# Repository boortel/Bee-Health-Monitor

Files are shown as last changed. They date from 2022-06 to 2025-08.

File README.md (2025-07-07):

# Bee Health Monitor project

The aim of this project is to design an open-source project, which would be done from commonly available modules using 3D printing technology.

## Which device is presented there?

This is a second version of the bee health monitor device, which was developed after evaluating the initial measurements with the original device. This version is designed to be realised by anyone at home with commonly available tools, hardware, and a 3D printer. The recommended print material is PETG or ASA as it provides good sunlight and weather durability and can be easily sterilised when moved to the other bee hive. The entire construction is made out of 6 printable parts and a single 2mm plexiglass. An acrylic varnish is applied to improve the water resistance. Using this device, dataset [Bee Dataset BUT-2](https://www.kaggle.com/datasets/imonbilk/bee-dataset-but-2) was collected. This device mounted on the beehive is shown in figure bellow:

Second version of *Bee health monitor* device

The chassis is mentioned to be mounted directly on the entrance to the hive in the way, so the bees are forced to use the 8mm long tunnels on the bottom of the device. The camera field of view is illuminated by a diffused warm white LED. The camera periodically senses bees when passing through the tunnels, as shown in figure bellow:

Sample from the image part of the dataset BUT-2.

The internal electronics consist of commonly available hobby electronic parts and RaspberryPi 4 as a control unit. The sensor equipment consists out of a camera, microphone, two humidity and temperature sensors intend to be placed inside the beehive, CO2 sensor, light sensor and an temperature, humidity and atmospheric pressure sensor to be positioned outside. All data are stored on an internal USB drive in a set interval, and the number of incoming and outgoing bees is evaluated from the camera capture. The main specifications of this device are shown in table bellow:

Device parameters.

## Related research papers

Besides the *Bee Health Monitor* platform, we would like to present our bee related research:

- Bee datasets
  - [Bee Dataset BUT-1](https://www.kaggle.com/datasets/imonbilk/bee-dataset-but-1): dataset collected with the first generation of our device. It contains only image data.
  - [Bee Dataset BUT-2](https://www.kaggle.com/datasets/imonbilk/bee-dataset-but-2): dataset collected with the second generation of our device. It contains image, sound and sensor data.
  - [Bee Dataset BUT-HS](https://www.kaggle.com/datasets/imonbilk/bee-dataset-but-hs): hyperspectral dataset containing images of bees, Varroa mites and detritus.
  - [Bee Dataset BUT-HS2](https://www.kaggle.com/datasets/masuel/bee-hyperspectral-dataset): dataset containing images of bees and Varroa mites under narrow spectra illumination used for the experiments with visual Varroa detection.
 
- Research papers
  -  [Visual Diagnosis of the Varroa Destructor Parasitic Mite in Honeybees Using Object Detector Techniques](https://www.mdpi.com/1424-8220/21/8/2764): article describing the Varroa mite detection using the YOLOv5 network.
  -  [Raspberry Pi Bee Health Monitoring Device](https://arxiv.org/abs/2304.14444): paper describing the communication and remote logging of the *Bee health monitor device*.
  -  [Machine learning and computer vision techniques in continuous beehive monitoring applications: A survey](https://www.sciencedirect.com/science/article/pii/S0168169923009481?dgcid=author): survey article focusing on the visual based bee health monitoring methods. A full version of the paper has a restricted access, a free preprint is available [here](https://arxiv.org/abs/2208.00085).
  -  [Computer Vision Approaches for Automated Bee Counting Application](https://www.sciencedirect.com/science/article/pii/S2405896324004580): paper comparing three possible approaches in the bee counting.
  -  [Varroa destructor detection on honey bees using hyperspectral imagery](https://www.sciencedirect.com/science/article/pii/S0168169924006100?dgcid=rss_sd_all): article describing a possible use of the hypespectral imaging in Varroa mite detection.
  -  [Towards Varroa destructor mite detection using a narrow spectra illumination](https://arxiv.org/abs/2504.06099): paper describing initial experiments with the narrow spectra illumination for Varroa mite detection.
 
- Final thesis
  - [Approximation of functions determining colony activity using neural networks](https://www.vut.cz/studenti/zav-prace/detail/151629): Master thesis describing the development of the setup presented in paper *Raspberry Pi Bee Health Monitoring Device* in a more detail together with further clustering experiments.
  - [Visual Detection of the Parasitic Mites on the Honeybee](https://www.vut.cz/en/students/final-thesis/detail/167591): Master thesis describing the development of the narrow spectra illumination unit and following experiments evolving the findings described in article *Varroa destructor detection on honey bees using hyperspectral imagery*. Summary of the thesis is presented in paper *Towards Varroa destructor mite detection using a narrow spectra illumination*.

## Software

The complete overview of the used software is provided in [software](https://github.com/boortel/Bee-Health-Monitor/tree/main/software) section.

## Hardware

The complete overview of device 3D printing, laser cutting, assembly and inner electrical installation is provided in [hardware](https://github.com/boortel/Bee-Health-Monitor/tree/main/hardware) section.

### Keywords

Bees, Health, Camera, Sensory, Neural Networks, AI

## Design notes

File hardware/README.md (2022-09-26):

# BeeLogger - Hardware setup

The folder contains a brief overview of how the device is constructed.
It contains the .STL and files of 3D printed parts, .DXF file of a laser-cut plastic window and a brief overview of how to assemble the entire device.
Also, the BOM of electronic componentes is apended.

## 3D Printed Parts and Laser Cut

Recommended 3D print infill ~15%

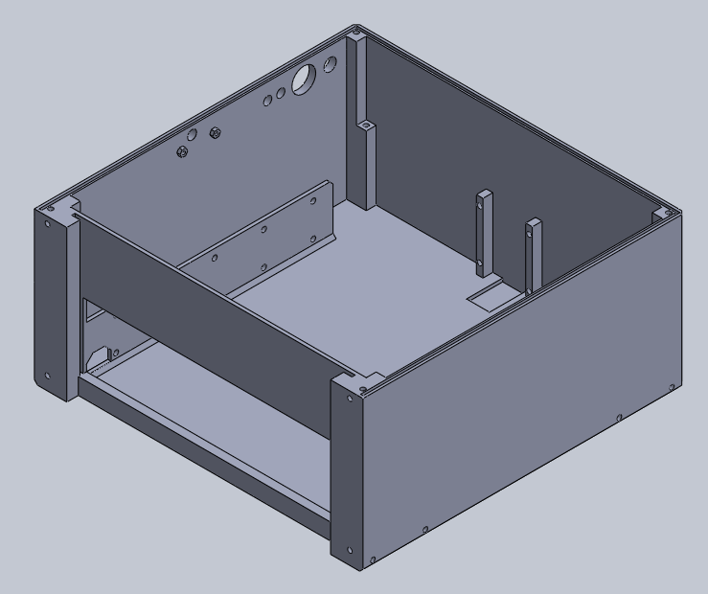
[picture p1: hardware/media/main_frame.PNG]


1x Main frame 

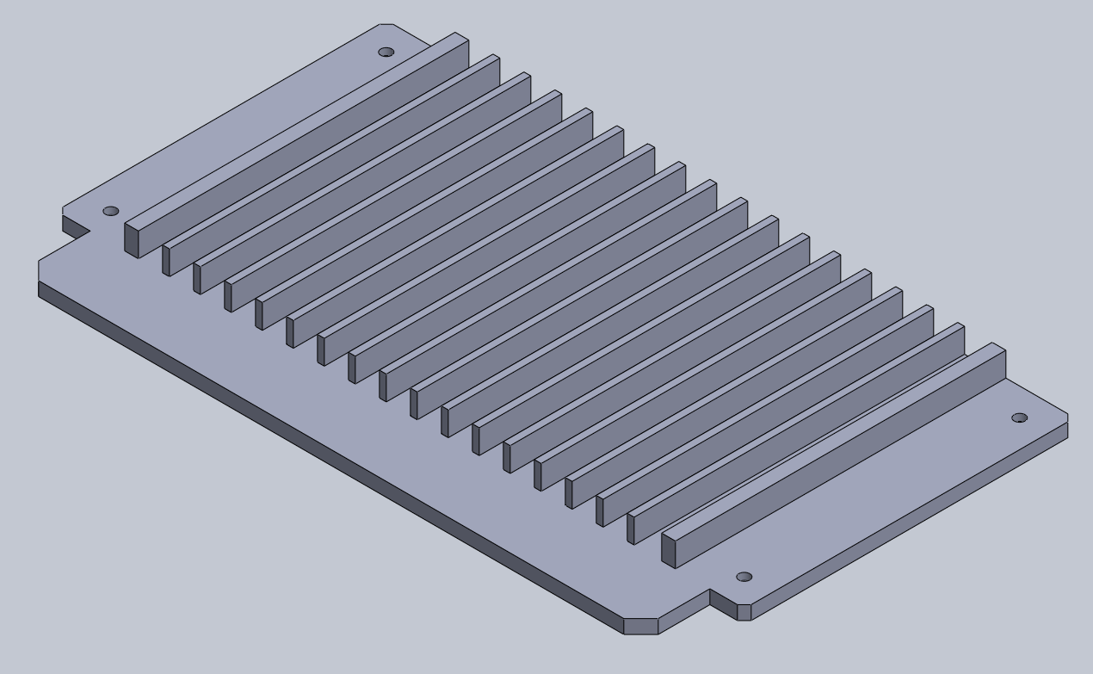
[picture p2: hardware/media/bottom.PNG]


1x Bottom (bee tunnels)

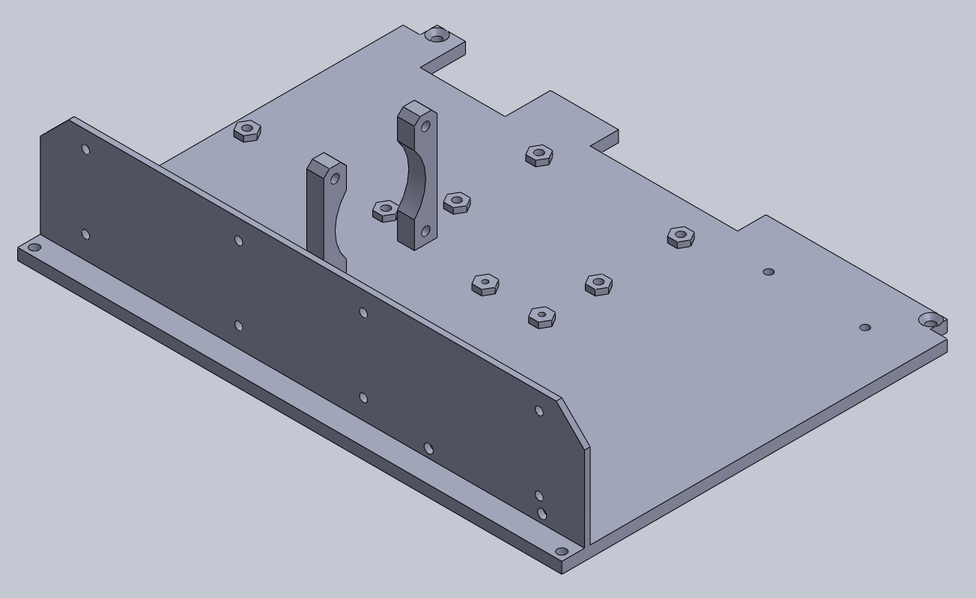
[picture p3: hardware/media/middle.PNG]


1x Middle (electronics mount layer)

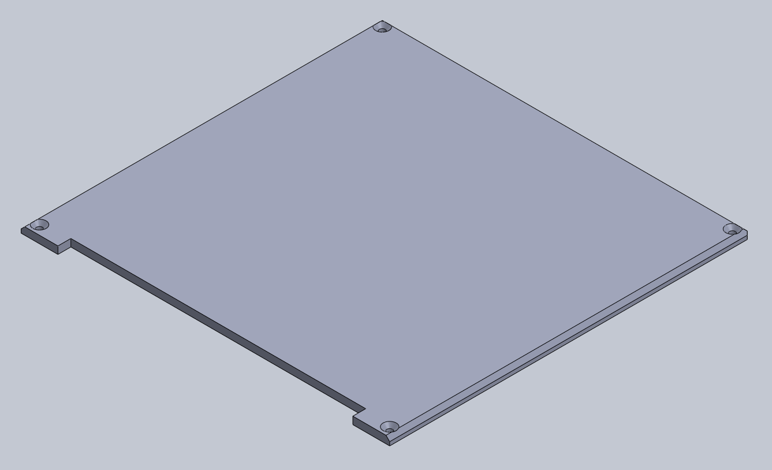
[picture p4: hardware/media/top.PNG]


1x Top cover

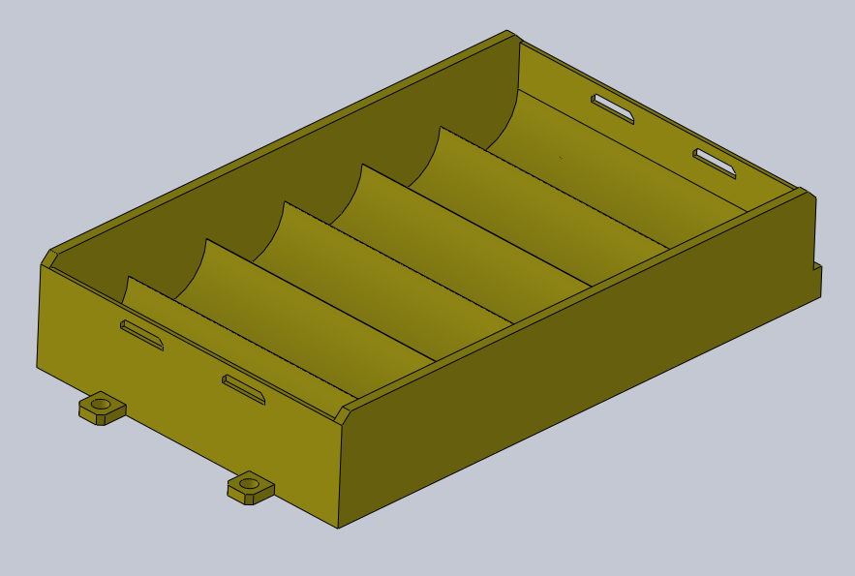
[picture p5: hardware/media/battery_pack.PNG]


1x Battery pack (6x 18650)

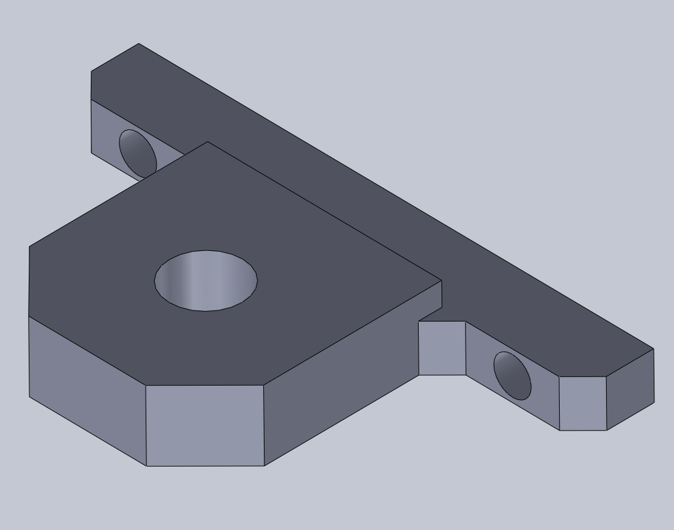
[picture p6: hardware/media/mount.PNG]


4x Helper mount hole

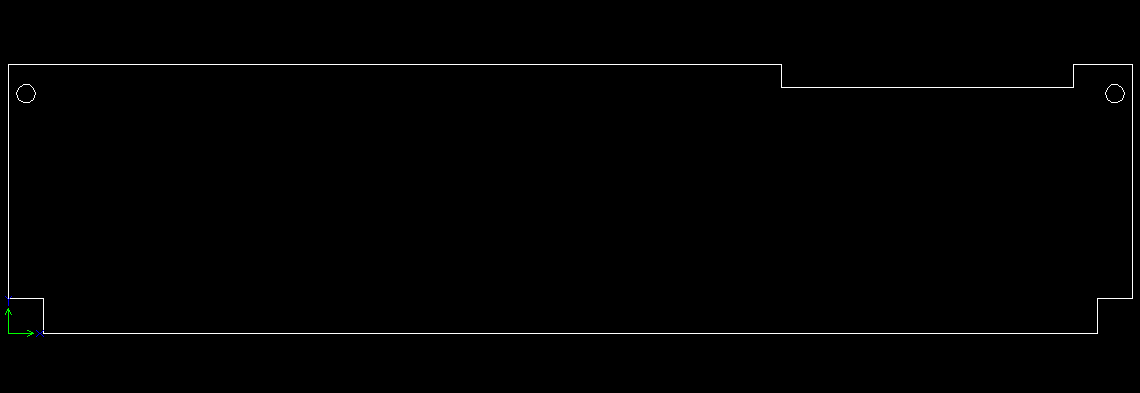
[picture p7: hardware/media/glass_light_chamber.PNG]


1x Laser-cut plastic window. Window suppose to be light diffuser and to be non-transparent. After cutting it, scratch it and glue white paper on it.

## Assembly

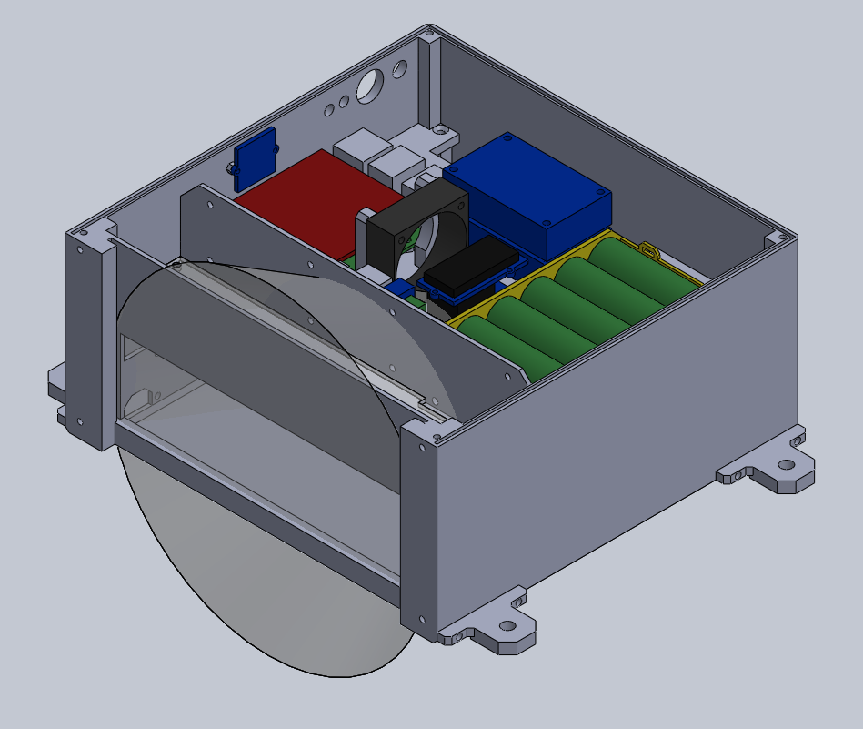
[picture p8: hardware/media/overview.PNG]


Inner layout of the assembled device

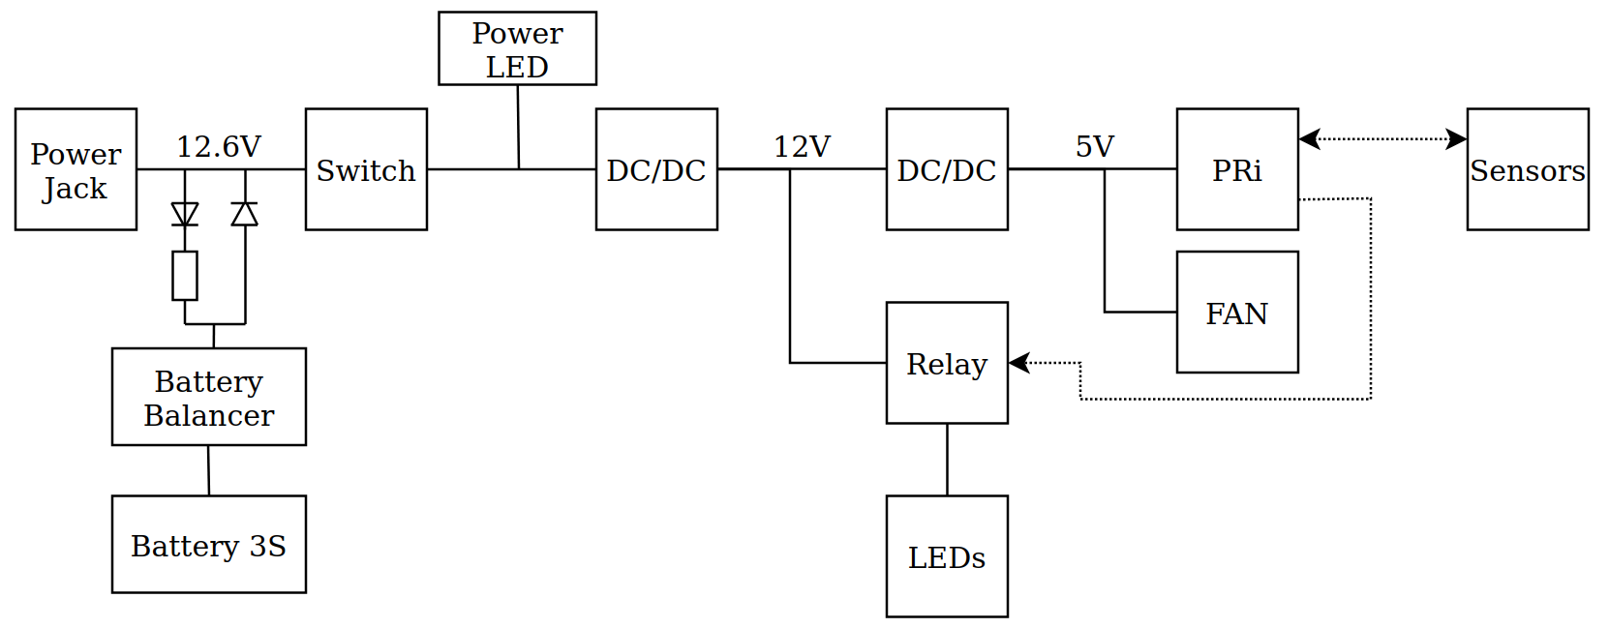
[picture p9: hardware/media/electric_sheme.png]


Electrical scheme. The battery resistor choose in the way, so the charging current will be between 1/10 and 1/100 of a battery capacity. 

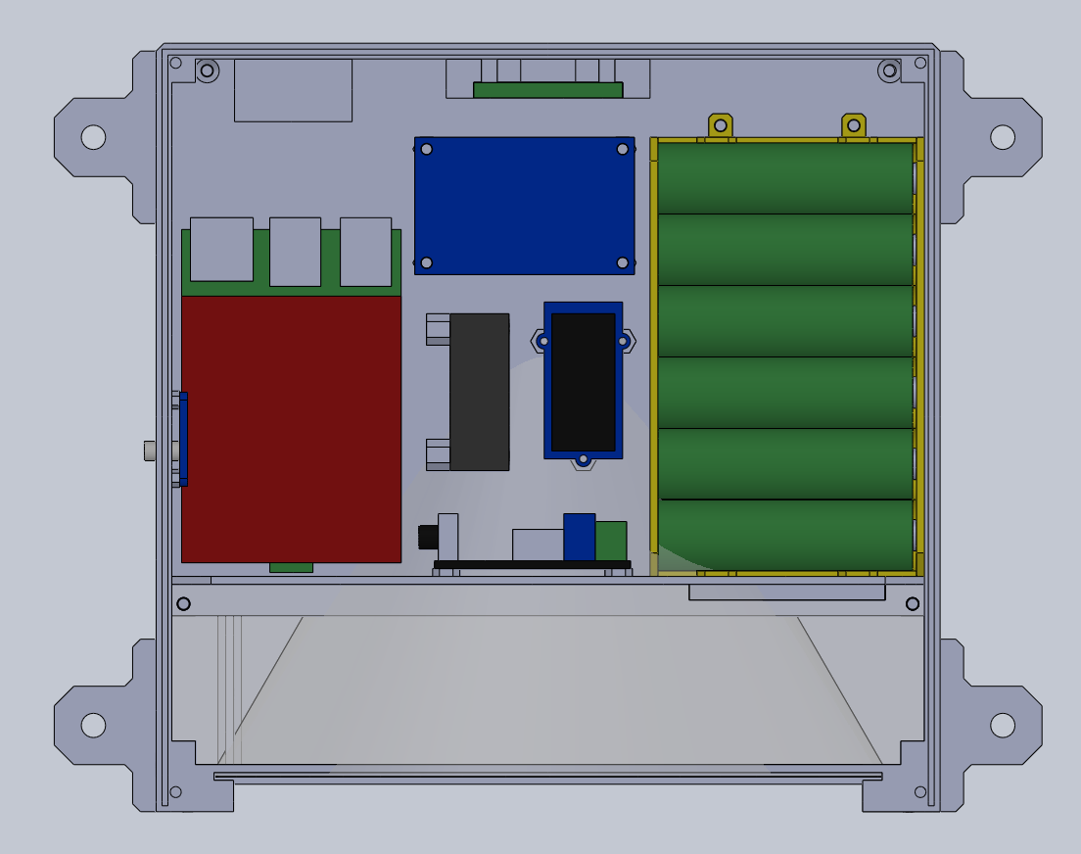
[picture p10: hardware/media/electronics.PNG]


Inner electronics layout

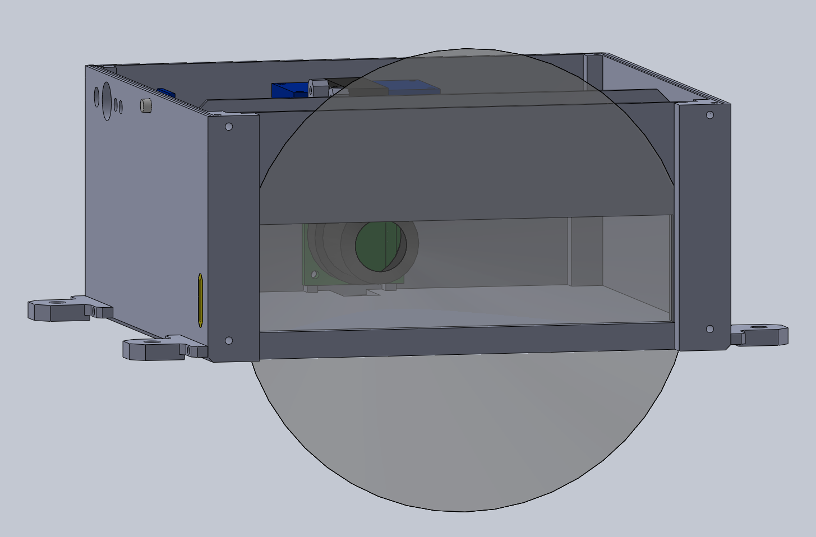
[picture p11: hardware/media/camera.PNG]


Camera's Filed of view

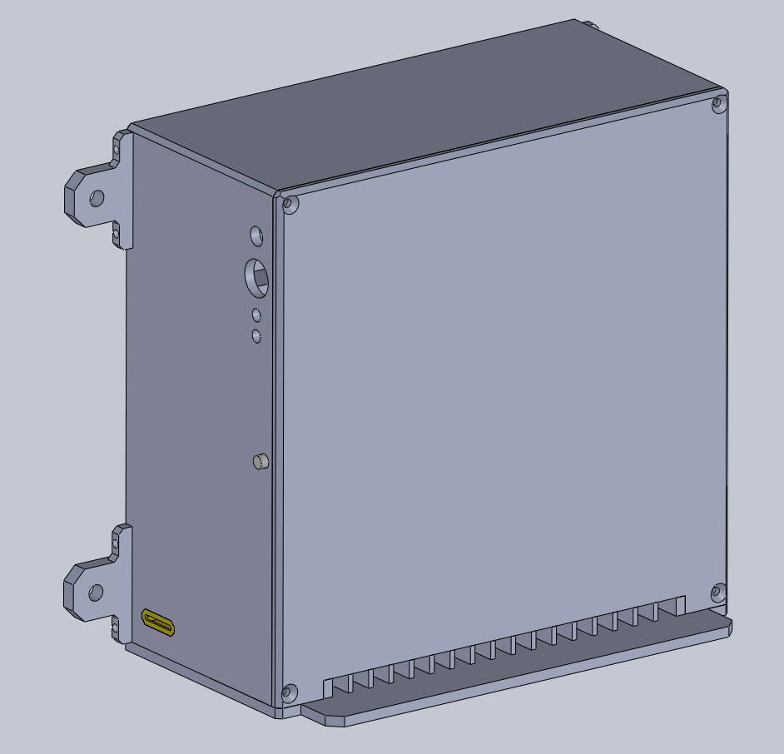
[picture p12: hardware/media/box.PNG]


General overview of the assembled device

## BOM

| Part                                                                                                                                                                                                                                                                                                                                                                                                                                                                                          | Quant. |
|-----------------------------------------------------------------------------------------------------------------------------------------------------------------------------------------------------------------------------------------------------------------------------------------------------------------------------------------------------------------------------------------------------------------------------------------------------------------------------------------------|--------|
| [Raspberry Pi 4](https://www.amazon.com/Raspberry-Model-2019-Quad-Bluetooth/dp/B07TC2BK1X/ref=sr_1_3?crid=3DNPLNTMRC0AU&keywords=raspberry+pi+4&qid=1657797906&sprefix=raspberry+pi+4%2Caps%2C250&sr=8-3)                                                                                                                                                                                                                                                                                     | 1      |
| [RPI HQ Cam](https://www.amazon.com/Arducam-Raspberry-Camera-Sensitivity-Adapter/dp/B09YHN5DBY/ref=sr_1_13?crid=3JH802ACAZP61&keywords=rpi+HQ+camera+lens&qid=1657798011&sprefix=rpi+hq+camera+len%2Caps%2C123&sr=8-13) + lens                                                                                                                                                                                                                                                                | 1      |
| [RPi Grove Shield](https://www.ebay.com/itm/334355129343?hash=item4dd91e63ff:g:mqgAAOSwQSJiJeLv)                                                                                                                                                                                                                                                                                                                                                                                              | 1      |
| [18650 Battery](https://www.amazon.com/dp/B0B6FSJ64C/ref=sr_1_6?keywords=18650+battery&qid=1657797820&s=hpc&sr=1-6)                                                                                                                                                                                                                                                                                                                                                                           | 6      |
| [Bat. Balancer](https://dratek.cz/arduino/1675-ochranny-modul-pro-li-ion-lithiovou-baterii-3s-11.1v-12.6v-25a.html?hp=&mena=2)                                                                                                                                                                                                                                                                                                                                                                | 1      |
| [DC/DC conv.](https://dratek.cz/arduino/1332-lm2596-buck-step-down-napajeci-modul-dc-4.0-40-1-3-37v-led-voltmetr.html)                                                                                                                                                                                                                                                                                                                                                                        | 2      |
| [Grove RTC](https://www.ebay.com/sch/i.html?_from=R40&_trksid=p2380057.m570.l1313&_nkw=grove+rtc&_sacat=0)                                                                                                                                                                                                                                                                                                                                                                                    | 1      |
| [DHT11](https://www.ebay.com/sch/i.html?_from=R40&_trksid=p2334524.m570.l1313&_nkw=DHT+11&_sacat=0&LH_TitleDesc=0&_odkw=grove+rtc&_osacat=0&LH_PrefLoc=2)                                                                                                                                                                                                                                                                                                                                     | 1      |
| [ENV3](https://rpishop.cz/senzory/4241-m5stack-env-iii-unit-se-senzorem-teploty-tlaku-a-vlhkosti-sht30qmp6988.html)                                                                                                                                                                                                                                                                                                                                                                           | 1      |
| [Grove Light Sensor](https://www.ebay.com/itm/115371780148?hash=item1adcb1a834:g:p5cAAOSw2lJijgGw&amdata=enc%3AAQAHAAAAsMwhKJOG7uEdWDz4aTTYPmgAQlXo4PAaFRxJYsTsN9ZDW8MtpcHMV4V%2Bhsg6oTzNw7bdYWFqKl9zcnKPQoEQt9o9jaSmYsWy3%2FuPxQbv%2F4rcpWA%2B3RqnVxn2d0qufJDMz87yKeJ0pvAH3CqHeBTu3Sl8CeBe4ytG7H0gK%2BD5vQbvUEcoCBuCv5cKKdVN2OFY7ayYmmd9%2BgUY6EnRWcesdm7kwgKTsANZybKgTvEvVADu%7Ctkp%3ABk9SR7TF1ce_YA)                                                                                       | 1      |
| [SGP30](https://www.ebay.com/itm/195140387077?hash=item2d6f460105:g:IV4AAOSwALliqovs&amdata=enc%3AAQAHAAAAoEYILUQBEA1M2qm9553zE1rYK8iZPUOqDFQ5M0U1%2F%2B7h1hD%2BO74fW6GdsqcuCPavIPDtD9BcmCXtbAdXqlqqsORFQD5AdWnqxj%2BqtnaFJ7cUh0A4W07rTO8RLcktgtYs15OxcXUyz%2BfB%2FDxUMdCkDCPD%2F7KCfHI3Wk3ZXtxuI%2BLa%2FMzSF8uARfPjLuD0sv1fOlyiwiupCzLwshgyeSRBeoM%3D%7Ctkp%3ABk9SR-yD3se_YA)                                                                                                                | 1      |
| [PWM module](https://www.gme.cz/pwm-regulator-6-28v-3a-product-38323)                                                                                                                                                                                                                                                                                                                                                                                                                         | 1      |
| White LED Strip (~5W)                                                                                                                                                                                                                                                                                                                                                                                                                                                                         | 1      |
| [Grove Relay](https://www.ebay.com/itm/254146781973?epid=22029928343&hash=item3b2c542315:g:EzMAAOSwSsZceRci&amdata=enc%3AAQAHAAAA4O%2B0Wh8ZB8VRDDb%2FWzsDqWErDy%2FSSafImfJD0wpvu4O8v7kF9CB2CKKtg%2BGMNghNTny%2FRScPLqYhwbOtqi4y3yHcN4Nm6020tmhc2842d%2FJ6y06LLDJvED1AmRqOSzUNlqRDt1n2pIq7CMECoP42DbTCAu3oM7Akx2VpHM4BNWExyj2piriykc%2FudUOkO0%2BGr6S1q3tQHmP1vzJkYcNNAeggqim%2Bv1iSXW%2F3%2FaeRGHtFIKr4Xokah2vNsq0NCE6vV5ECmTIgx4qSGdqW1niWqcfyO4UyeRj%2BD3lZ4KXjOPj%2B%7Ctkp%3ABFBMhq7lx79g) | 1      |
| [Fan 40mm 5V](https://www.ebay.com/itm/193494700157?hash=item2d0d2ed07d:g:~h4AAOSwHXxe5R9a&amdata=enc%3AAQAHAAAA4MZ8QLBYeV7MZkPQ7aCef%2FeS%2BUYi0dzfAXOKBU7Zo4sm7spztomIV5cc2MlaOlDPu42ZvmNDGqQX%2B3mkWMrqmf3cN8Dlz27DkY55V6tVkCSmj6hSFUPBTyDseW5LpGHNnjDxnF37DiYTF8kNNkPfArd9EyDPTwA9pWbKx5dlC7pIH6vvy20zI56Copqv5gKE573sLwvWoSqf3IbCN%2BPLXv6VAXJj%2FiGKq7W7P5nI7lhjMEqyEEVWnVKuz9BdJLZP9Y290r86Uu6Ve5wx2erYl9JlciHpBKVwx%2BlAuhTlekcO%7Ctkp%3ABFBM0tXnx79g)                                | 1      |
| [Mic](https://www.ebay.com/itm/354075600684?epid=114811768&hash=item52708ce72c:g:XxAAAOSwwPphWdPQ&amdata=enc%3AAQAHAAAA0MovSSj2B8fCi1UciKMQTruINFD31l0nOGRFHE60S58GoFakqbGCcVotesylyoWFaqIN5MyUQbZzAnNIb0QimNdfYYf2y5Rr0zYdyH%2Fhfd8kVY8AievarkFtJ1cfjrMB8Z52GJsmWBXqa8CGebM%2BvAJqmdpOzCz9i%2BnuoDnG8mN28lzAJt925zVX%2BlFu2YwtTvOwF9b7tAyrJPX1JeAMaM%2FUv9zJn1R%2B%2BnNvEcAJSrfwgm3JkXlF4zdoKQmj9zJJT2a4a20MygMvFRIiBA%2BrXtI%3D%7Ctkp%3ABFBM7rrW0sJg)                                       | 1      |
| M2.5x6 screws                                                                                                                                                                                                                                                                                                                                                                                                                                                                                 | ~ 10   |
| M3x6 screws                                                                                                                                                                                                                                                                                                                                                                                                                                                                                   | ~ 30   |

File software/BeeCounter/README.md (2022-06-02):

# Bee tracker (FicekD)

Please see the original repository: https://github.com/FicekD/Bee-Tracking

This software implements counting of the bees arriving and leaving a hive through the measuring device. Version used in this repository is not a stand-alone application and it does not contain any visualisation tools.

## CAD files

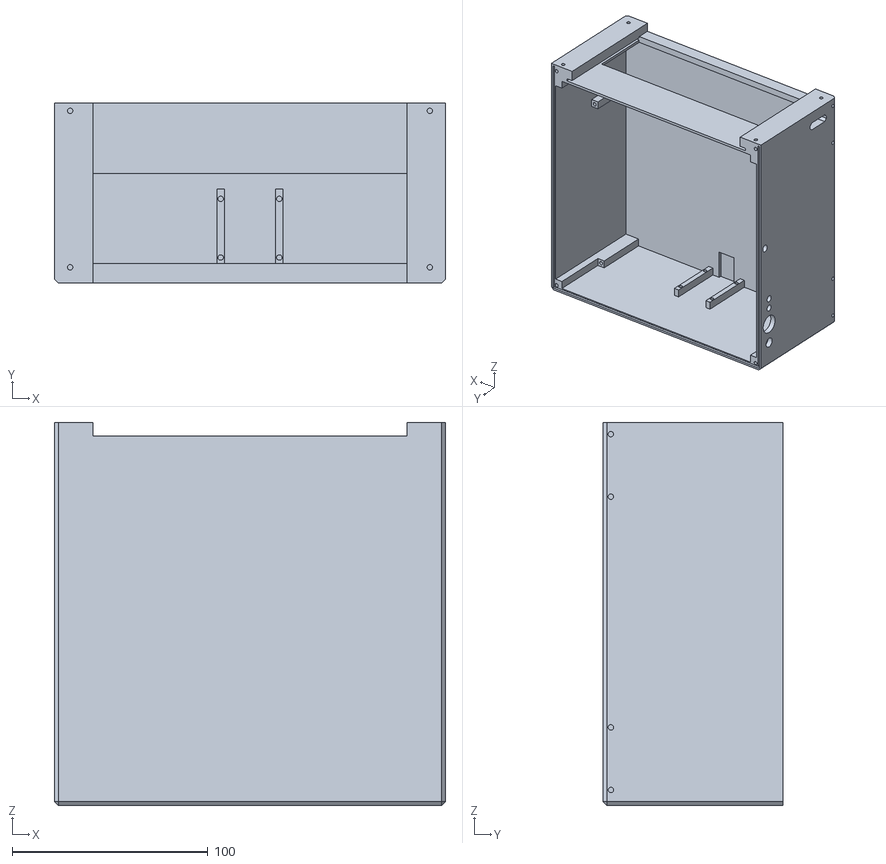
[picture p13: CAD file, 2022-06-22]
hardware/stls/main_frame.STL
200.0 x 92.0 x 196.0

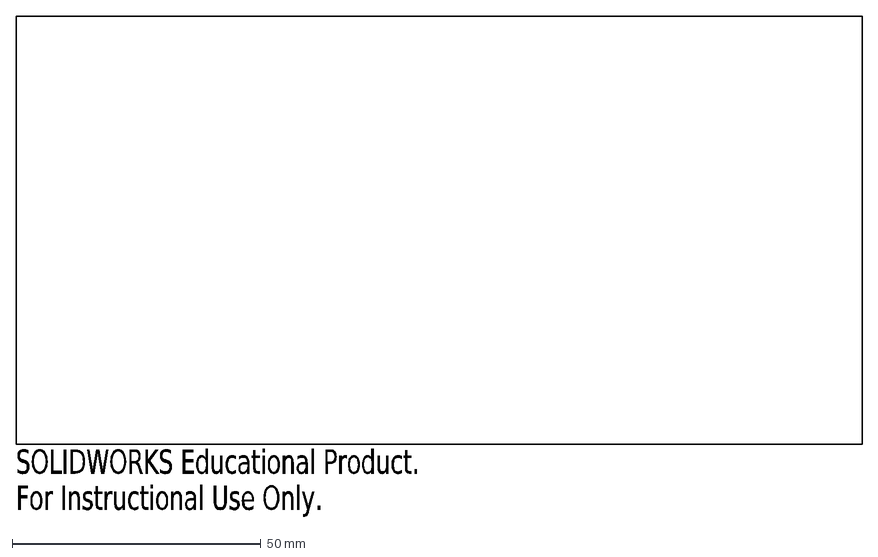
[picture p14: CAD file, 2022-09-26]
hardware/laser_cut/glass.DXF
SOLIDWORKS Educational Product.
For Instructional Use Only.

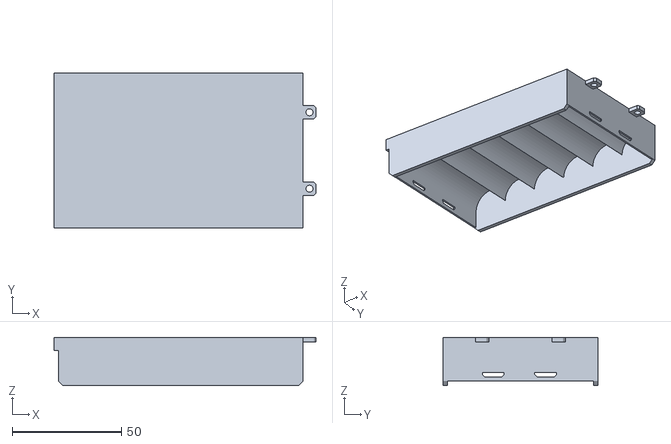
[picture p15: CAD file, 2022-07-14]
hardware/stls/battery_pack.STL
120.0 x 71.0 x 22.0

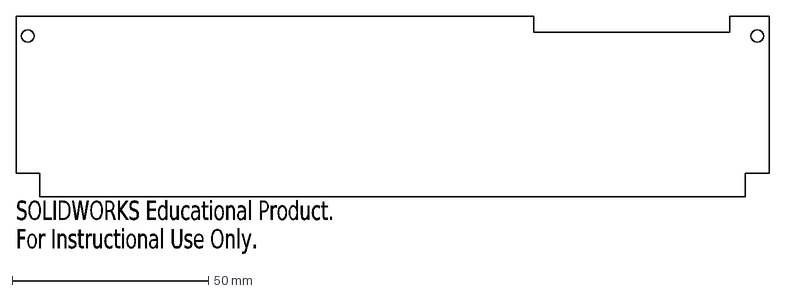
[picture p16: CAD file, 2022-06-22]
hardware/laser_cut/glass_light_chamber.DXF
SOLIDWORKS Educational Product.
For Instructional Use Only.

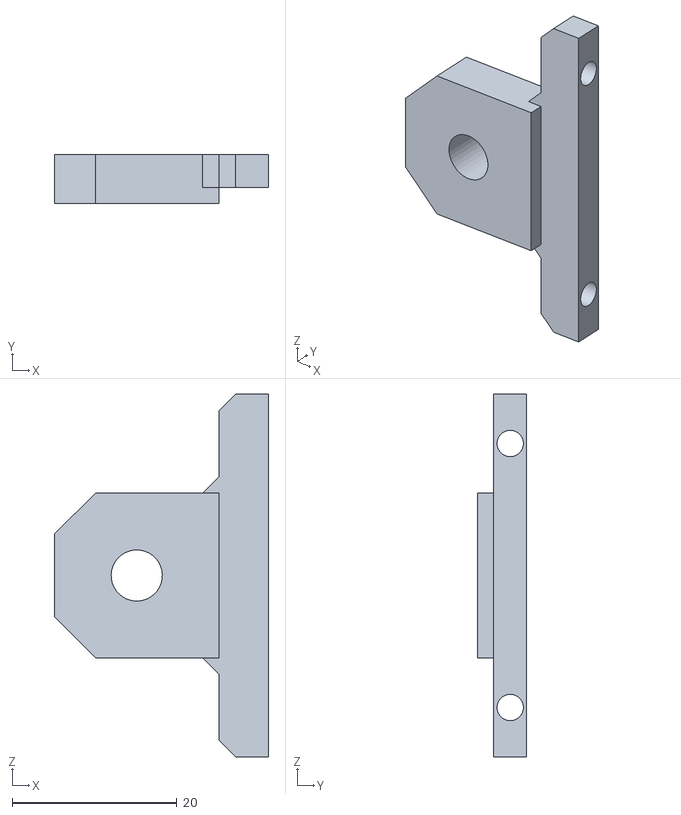
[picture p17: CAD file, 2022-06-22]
hardware/stls/mount.STL
26.0 x 6.00 x 44.0

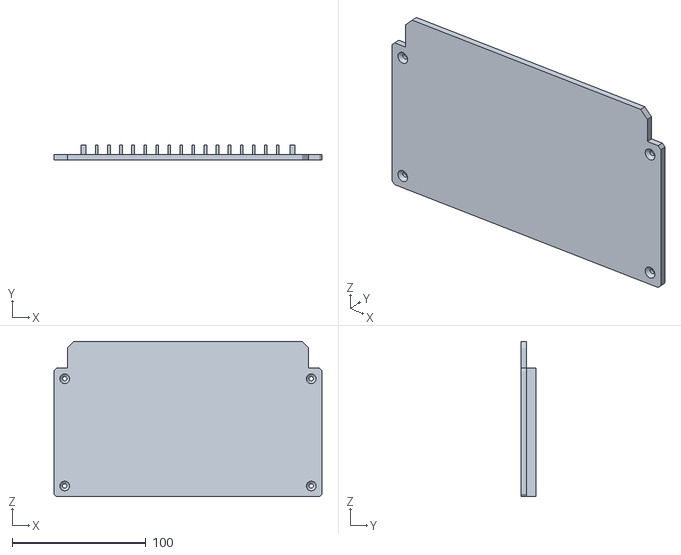
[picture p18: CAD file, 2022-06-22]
hardware/stls/bottom.STL
200.0 x 11.0 x 116.0

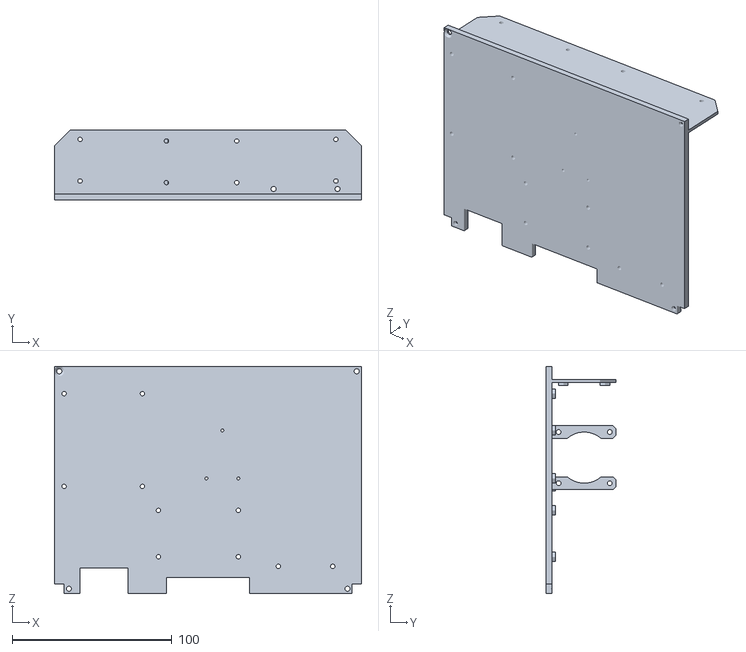
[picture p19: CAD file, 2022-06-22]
hardware/stls/middle.STL
192.0 x 44.0 x 142.0

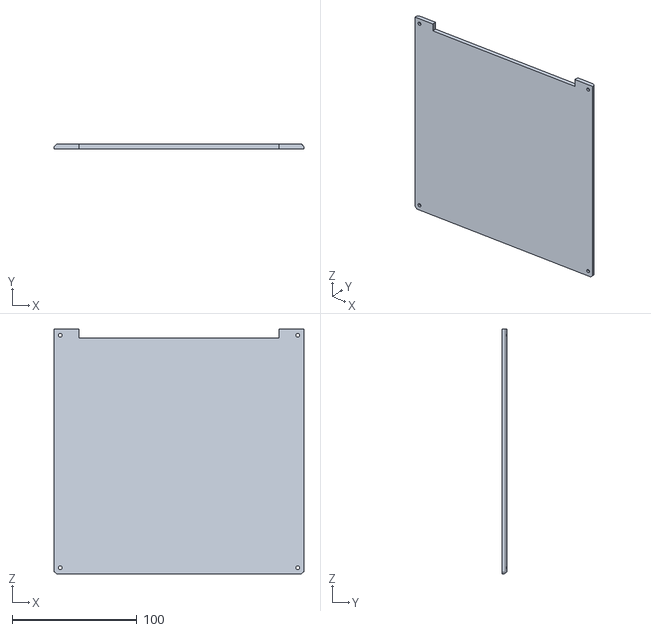
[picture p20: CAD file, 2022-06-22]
hardware/stls/top.STL
200.0 x 4.00 x 196.0

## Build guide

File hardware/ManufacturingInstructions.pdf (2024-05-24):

# Bee health monitor manufacturing instructions

Instructions valid for version 2.1. (summer 2023) | May 2024
| Brno, Czech Republic

## List of contents

## 1. Responsibility disclaimer

Building and using of the proposed device is at your own responsibility. We do not take any responsibility of damage caused by building, or using the Bee Health Monitor device. All information, content, and materials available in this project are for general informational purposes only.

## 2. Introduction

This document describes the assembly of the Bee Health monitor device. Due to the intention of long-term in field measurements, please read this document carefully so you could avoid damaging your device. Basic knowledge in electronics, 3D printing and DYI stuff is needed for the device assembly. Minor deviations from the provided instructions and schemes are possible.
The instructions are valid for the version from summer 2023.

## 3. Preparation phase

This chapter describes the required steps prior the mechanical and electrical assembly.

### 3.1. Electronic modules preparations

Prepare the PWM module, DC-DC convertor, rPi camera, rPi4 and the sensor modules as shown in Figure 1. Fill all connectors with electric insulating vaseline (preferably TPFE) and paint the circuit boards with a suitable varnish designed for the use on electronics. This is required to avoid potential damage caused by humidity. Be careful not to paint over camera chip or any contacts.

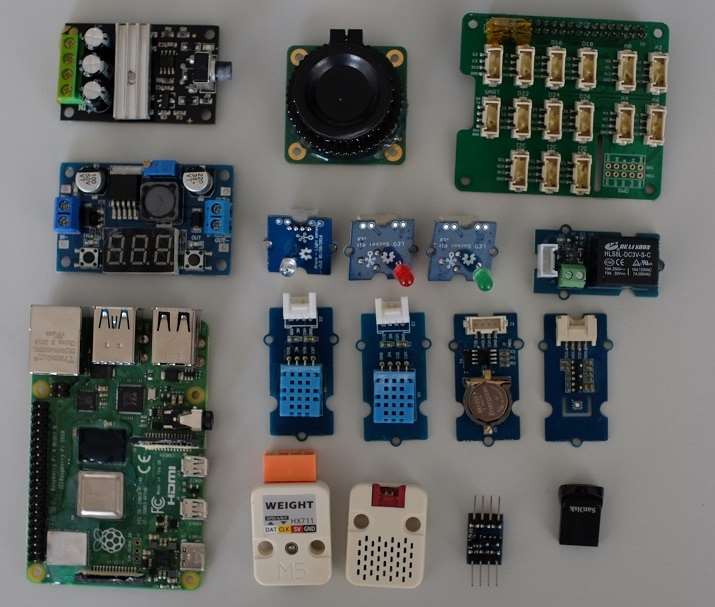
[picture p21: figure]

Figure 1 Required HW and electronic modules As few of the rPi chips and components are BGAs, please seal their surroundings using silicone intended for electronics. Mounting passive cooling is also recommended.

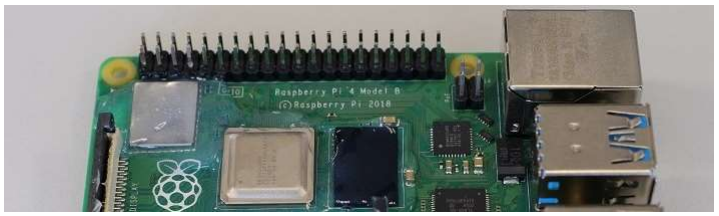
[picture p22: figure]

Figure 2 MCU sealings

### 3.2. Mechanical part preparations

Print all the 3D parts from the Bee-Health-Monitor/hardware/stls/ directory. Prepare the LED strip on aluminum plate and cut the M3 threads to the plate. Prepare the laser cut plexiglas from the directory Bee-Health-Monitor/hardware/laser_cut/ and brush the diffusing plate as shown in Figure 3.

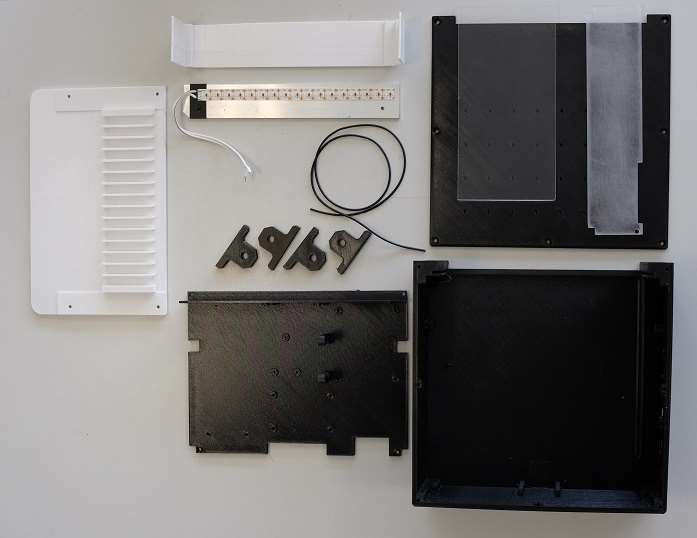
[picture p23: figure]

Figure 3 Printed 3D parts, laser cuts, LED plate and sealing gasket The main box and cover should be sprayed with a primer varnish with filler to seal small gaps caused by the 3D printing. The back side of cover plate and the inner side of the box opposite the diffuser plate should be painted with a matt white to improve the illumination conditions (diffuse the light) as shown in Figure 4.
After spraying the exterior of the main box and cover with a primer, use an acrylic varnish of a proper color to improve the protection and place the sealing gasket to the rabbet in the main box.

## 4. Mechanical assembly

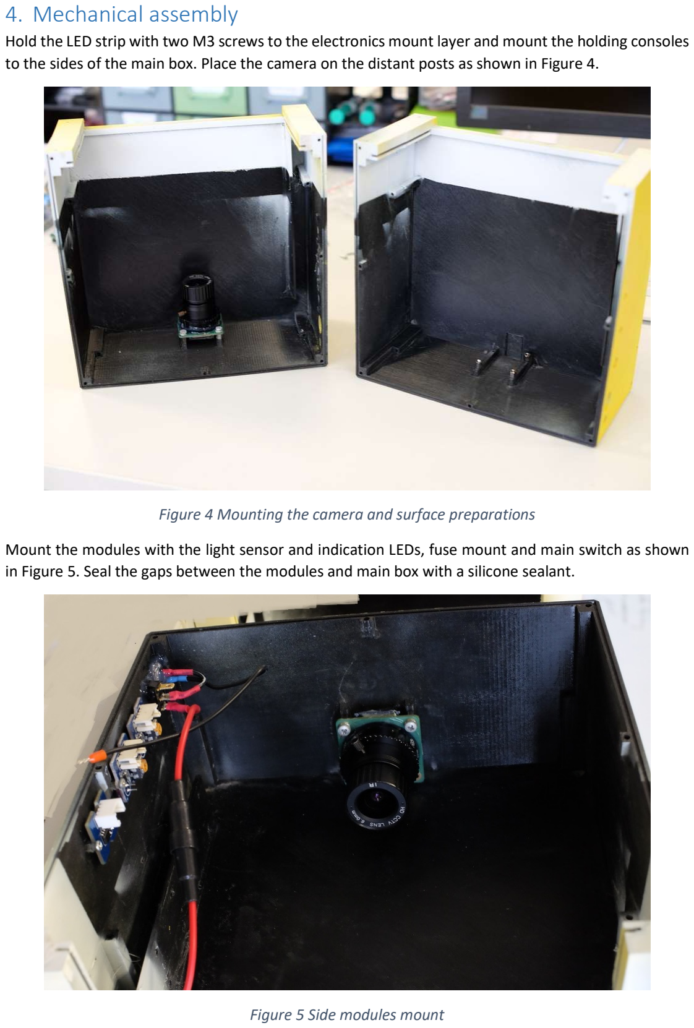
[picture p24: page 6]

Hold the LED strip with two M3 screws to the electronics mount layer and mount the holding consoles to the sides of the main box. Place the camera on the distant posts as shown in Figure 4.

Figure 4 Mounting the camera and surface preparations Mount the modules with the light sensor and indication LEDs, fuse mount and main switch as shown in Figure 5. Seal the gaps between the modules and main box with a silicone sealant.

Figure 5 Side modules mount

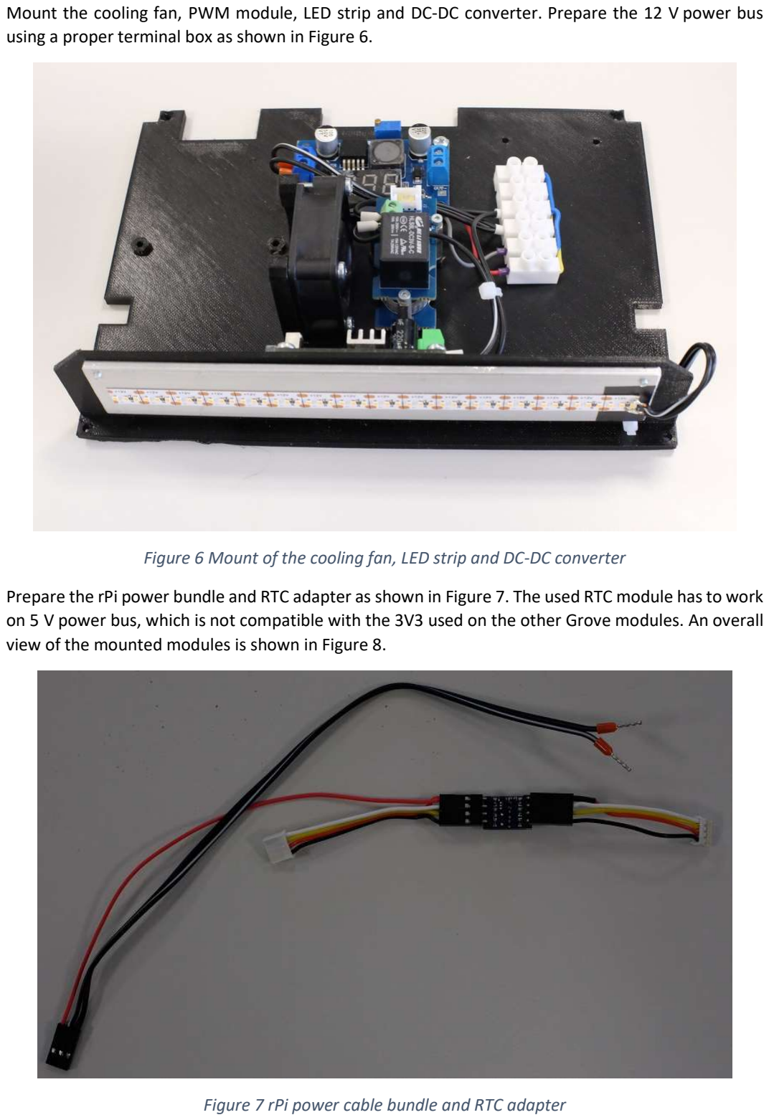
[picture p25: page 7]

Mount the cooling fan, PWM module, LED strip and DC-DC converter. Prepare the 12 V power bus using a proper terminal box as shown in Figure 6.

Figure 6 Mount of the cooling fan, LED strip and DC-DC converter Prepare the rPi power bundle and RTC adapter as shown in Figure 7. The used RTC module has to work on 5 V power bus, which is not compatible with the 3V3 used on the other Grove modules. An overall view of the mounted modules is shown in Figure 8.

Figure 7 rPi power cable bundle and RTC adapter

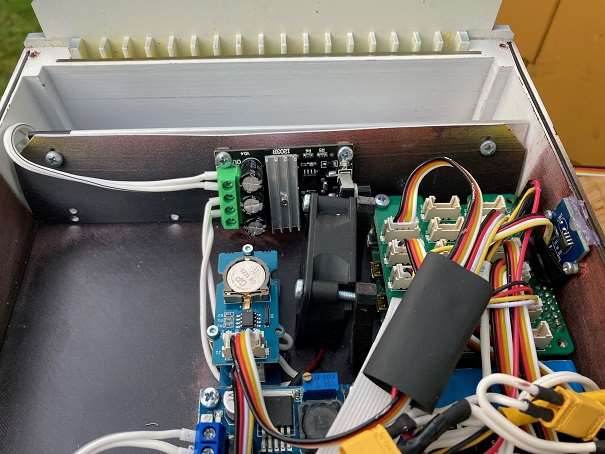
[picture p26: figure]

Figure 8 Overall assembly of interval electronics

## 5. Electrical assembly

Connect the modules and sensors as shown in Figure 9. Seal the sensor grommet to avoid entrance of the bees to the device. Charger module and internal battery is not used in the version 2.1 anymore. Load the SW and test the whole assembly using a monitor, keyboard and mouse. If everything works, focus the camera and mount the front cover to the device.

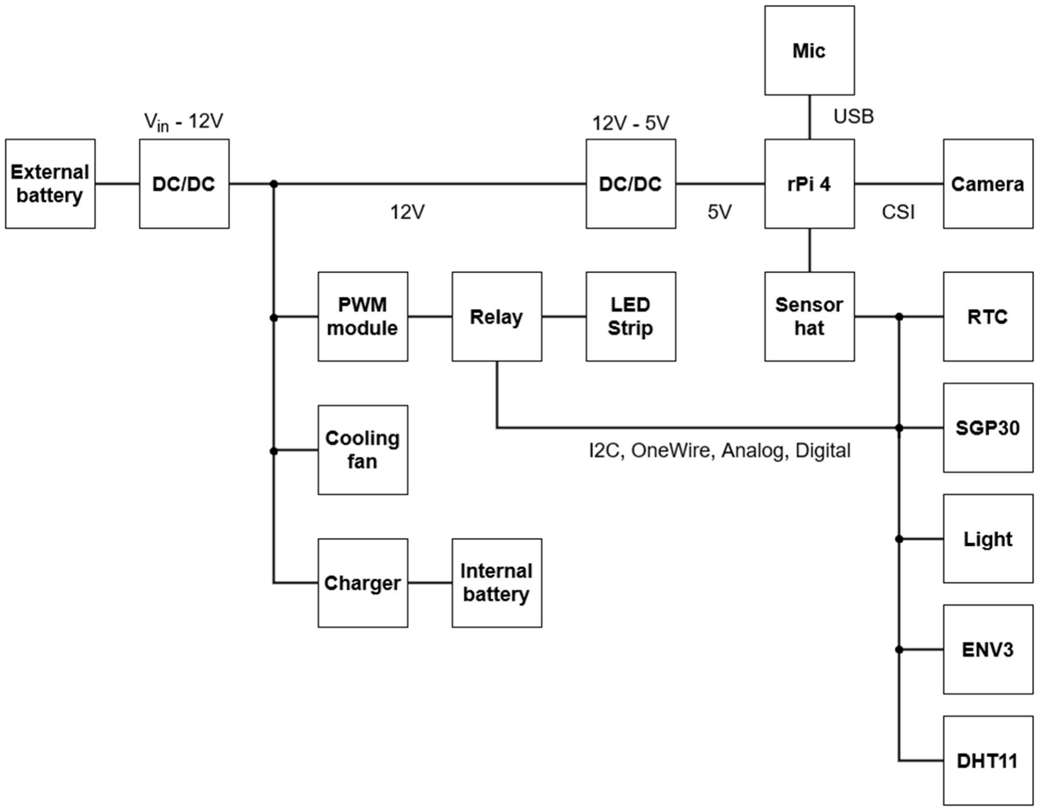
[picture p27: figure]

Figure 9 Block scheme of the electrical assembly

## 6. Mounting the device to the hive

Mount the device to the beehive as shown in Figure 10. If you provide the power supply with the power adapter and the electrical grid, keep the safety regulations for powering the device in the outdoor conditions to avoid a risk of an injury.

1.

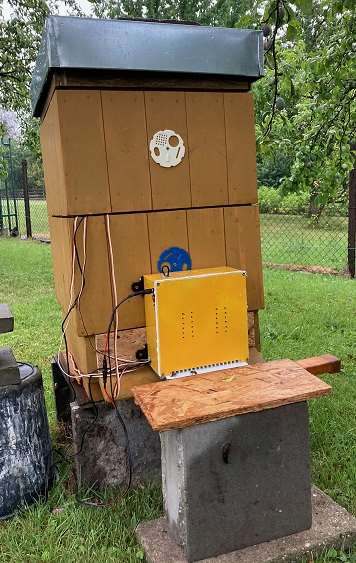
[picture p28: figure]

Figure 10 Bee health monitor in front of the hive

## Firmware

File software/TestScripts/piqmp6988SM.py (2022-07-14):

# -*- coding: utf-8 -*-
#import pigpio
from grove.i2c import Bus
from smbus2 import SMBus, i2c_msg, I2cFunc
import time
from enum import Enum

SMBUS = True
DEBUG = False

# QMP6988の値を扱う処理の詳細はデータシートを参照
ADDRESS_0            = 0x70
ADDRESS_1            = 0x56

TEMP_TXD0            = 0xFC
TEMP_TXD1            = 0xFB
TEMP_TXD2            = 0xFA
PRESS_TXD0           = 0xF9
PRESS_TXD1           = 0xF8
PRESS_TXD2           = 0xF7
IO_SETUP             = 0xF5
CTRL_MEAS            = 0xF4
DEVICE_STAT          = 0xF3
I2C_SET              = 0xF2
IIR_CNT              = 0xF1
RESET                = 0xE0
CHIP_ID              = 0xD1
COE_b00_a0_ex        = 0xB8
COE_a2_0             = 0xB7
COE_a2_1             = 0xB6
COE_a1_0             = 0xB5
COE_a1_1             = 0xB4
COE_a0_0             = 0xB3
COE_a0_1             = 0xB2
COE_bp3_0            = 0xB1
COE_bp3_1            = 0xB0
COE_b21_0            = 0xAF
COE_b21_1            = 0xAE
COE_b12_0            = 0xAD
COE_b12_1            = 0xAC
COE_bp2_0            = 0xAB
COE_bp2_1            = 0xAA
COE_b11_0            = 0xA9
COE_b11_1            = 0xA8
COE_bp1_0            = 0xA7
COE_bp1_1            = 0xA6
COE_bt2_0            = 0xA5
COE_bt2_1            = 0xA4
COE_bt1_0            = 0xA3
COE_bt1_1            = 0xA2
COE_b00_0            = 0xA1
COE_b00_1            = 0xA0

SUBTRACTOR           = 8388608 # (2 ** 23)

REG_COE              = COE_b00_1
COE_LENGTH           = 25

REG_CHIP_ID          = CHIP_ID
CHIP_ID_LENGTH       = 1

REG_RESET            = RESET
RESET_VALUE          = 0xE6

REG_CTRL_MEAS        = CTRL_MEAS
CTRL_MEAS_LENGTH     = 1

REG_IIR_CNT          = IIR_CNT
IIR_CNT_LENGTH       = 1

REG_DATA             = PRESS_TXD2
DATA_LENGTH          = 6

class Coe(Enum):
    b00_1            = 0
    b00_0            = 1
    bt1_1            = 2
    bt1_0            = 3
    bt2_1            = 4
    bt2_0            = 5
    bp1_1            = 6
    bp1_0            = 7
    b11_1            = 8
    b11_0            = 9
    bp2_1            = 10
    bp2_0            = 11
    b12_1            = 12
    b12_0            = 13
    b21_1            = 14
    b21_0            = 15
    bp3_1            = 16
    bp3_0            = 17
    a0_1             = 18
    a0_0             = 19
    a1_1             = 20
    a1_0             = 21
    a2_1             = 22
    a2_0             = 23
    b00_a0_ex        = 24

class Address(Enum):
    LOW              = ADDRESS_0    
    HIGH             = ADDRESS_1    

class Powermode(Enum):
    SLEEP            = 0
    FORCE            = 1
    NORMAL           = 3

class Filter(Enum):
    COEFFECT_OFF     = 0
    COEFFECT_2       = 1
    COEFFECT_4       = 2
    COEFFECT_8       = 3
    COEFFECT_16      = 4
    COEFFECT_32      = 5

class Oversampling(Enum):
    SKIP             = 0
    X1               = 1
    X2               = 2
    X4               = 3
    X8               = 4
    X16              = 5
    X32              = 6
    X64              = 7

class Data(Enum):
    PRESS_TXD2       = 0
    PRESS_TXD1       = 1
    PRESS_TXD0       = 2
    TEMP_TXD2        = 3
    TEMP_TXD1        = 4
    TEMP_TXD0        = 5

K_PARAM = {
    'a0'  : { 'A' :  0.0     , 'S' : 1.0     , 'D' :    16.0 },    
    'a1'  : { 'A' : -6.30E-03, 'S' : 4.30E-04, 'D' : 32767.0 },    
    'a2'  : { 'A' : -1.90E-11, 'S' : 1.20E-10, 'D' : 32767.0 },    
    'b00' : { 'A' :  0.0     , 'S' : 1.0     , 'D' :    16.0 },    
    'bt1' : { 'A' :  1.00E-01, 'S' : 9.10E-02, 'D' : 32767.0 },    
    'bt2' : { 'A' :  1.20E-08, 'S' : 1.20E-06, 'D' : 32767.0 },    
    'bp1' : { 'A' :  3.30E-02, 'S' : 1.90E-02, 'D' : 32767.0 },    
    'b11' : { 'A' :  2.10E-07, 'S' : 1.40E-07, 'D' : 32767.0 },    
    'bp2' : { 'A' : -6.30E-10, 'S' : 3.50E-10, 'D' : 32767.0 },    
    'b12' : { 'A' :  2.90E-13, 'S' : 7.60E-13, 'D' : 32767.0 },    
    'b21' : { 'A' :  2.10E-15, 'S' : 1.20E-14, 'D' : 32767.0 },    
    'bp3' : { 'A' :  1.30E-16, 'S' : 7.90E-17, 'D' : 32767.0 }    
}

class PiQmp6988(object):
    def __init__(self, config={}):
        self.k  = {}
        self.config = {}
        self.bus = Bus(1)
        time.sleep(0.02)
        config_i = {
            'address' : Address.LOW.value,
            'filter' : Filter.COEFFECT_OFF.value,
            'mode': Powermode.SLEEP.value,
            'pressure' : Oversampling.SKIP.value,
            'temperature' : Oversampling.SKIP.value
        }
        self.__modify_config(config_i)
        self.__modify_config(config)
        self.__pre_process()

      
        # QMP6988から各レジスタの値を読み出す
        if SMBUS:
            if DEBUG:
                print('Attempt to read ID')
            data = self.bus.read_i2c_block_data(self.config['address'], REG_CHIP_ID, CHIP_ID_LENGTH)
            if DEBUG:
                print('Read ID')
                print(data)
        else:
            len, data = self.pi.i2c_read_i2c_block_data(self.qmp6988, REG_CHIP_ID, CHIP_ID_LENGTH)

        # キャリブレーションデータを読み出す
        if SMBUS:
            if DEBUG:
                print('Attempt to read coefs')
            data = self.bus.read_i2c_block_data(self.config['address'], REG_COE, COE_LENGTH)
            if DEBUG:
                print('Read coefs')
                for d in data:
                   print(d)
        else:
            len, data = self.pi.i2c_read_i2c_block_data(self.qmp6988, REG_COE, COE_LENGTH)
        
        # 係数を計算する
        self.__initialize_k(data)
        
        # 設定を反映する
        self.__apply_config()

        #self.__post_process()

    def __pre_process(self):
        """
        pigpioを初期化してQMP6988との接続を初期化する．
        """

        if SMBUS:
            self.bus.instance.open(1)
            time.sleep(0.02)
        else:
            self.pi = pigpio.pi()
            # I2C bus
            self.qmp6988 = self.pi.i2c_open(1, self.config['address'])


    def __post_process(self):
        """
        pigpioを終了してQMP6988との接続を切断する．
        """
        if SMBUS:
            #self.bus.instance.close()
            temptemp=1
        else:
            self.pi.i2c_close(self.qmp6988)
            self.pi.stop()

    def __modify_config(self, config={}):
        """
        設定を変更する．
        """
        for key in config.keys():
            if config[key] is not None:
                self.config[key] = config[key]

    def __apply_config(self):
        """
        レジスタに設定値を反映する．
        """
        self.__set_powermode(self.config['mode'])
        self.__set_filter(self.config['filter'])
        self.__set_oversampling('temperature', self.config['temperature'])
        self.__set_oversampling('pressure', self.config['pressure'])

    def __calc_k(self, index, otp):
        return K_PARAM[index]['A'] + (K_PARAM[index]['S'] * otp) / K_PARAM[index]['D'] 

    def __initialize_k(self, data):
        """
        OTPの値から係数を算出する．
        """
        otp = (data[Coe.a0_1.value] << 12) | (data[Coe.a0_0.value]) << 4 | (data[Coe.b00_a0_ex.value] & 0x0F)
        otp = self.__convert_signed(otp, 19)
        self.k['a0'] = self.__calc_k('a0', otp)
        K_PARAM['a0']['OTP'] = otp
        
        otp = (data[Coe.a1_1.value] << 8) | (data[Coe.a1_0.value])
        otp = self.__convert_signed(otp, 15)
        self.k['a1'] = self.__calc_k('a1', otp)
        K_PARAM['a1']['OTP'] = otp
        
        otp = (data[Coe.a2_1.value] << 8) | (data[Coe.a2_0.value])
        otp = self.__convert_signed(otp, 15)
        self.k['a2'] = self.__calc_k('a2', otp)
        K_PARAM['a2']['OTP'] = otp
        
        otp = (data[Coe.b00_1.value] << 12) | (data[Coe.b00_0.value]) << 4 | ((data[Coe.b00_a0_ex.value] & 0xF0) >> 4)
        otp = self.__convert_signed(otp, 19)
        self.k['b00'] = self.__calc_k('b00', otp)
        
        otp = (data[Coe.bt1_1.value] << 8) | (data[Coe.bt1_0.value])
        otp = self.__convert_signed(otp, 15)
        self.k['bt1'] = self.__calc_k('bt1', otp)
        
        otp = (data[Coe.bt2_1.value] << 8) | (data[Coe.bt2_0.value])
        otp = self.__convert_signed(otp, 15)
        self.k['bt2'] = self.__calc_k('bt2', otp)
        
        otp = (data[Coe.bp1_1.value] << 8) | (data[Coe.bp1_0.value])
        otp = self.__convert_signed(otp, 15)
        self.k['bp1'] = self.__calc_k('bp1', otp)
        
        otp = (data[Coe.b11_1.value] << 8) | (data[Coe.b11_0.value])
        otp = self.__convert_signed(otp, 15)
        self.k['b11'] = self.__calc_k('b11', otp)
        
        otp = (data[Coe.bp2_1.value] << 8) | (data[Coe.bp2_0.value])
        otp = self.__convert_signed(otp, 15)
        self.k['bp2'] = self.__calc_k('bp2', otp)
        
        otp = (data[Coe.b12_1.value] << 8) | (data[Coe.b12_0.value])
        otp = self.__convert_signed(otp, 15)
        self.k['b12'] = self.__calc_k('b12', otp)
        
        otp = (data[Coe.b21_1.value] << 8) | (data[Coe.b21_0.value])
        otp = self.__convert_signed(otp, 15)
        self.k['b21'] = self.__calc_k('b21', otp)
        
        otp = (data[Coe.bp3_1.value] << 8) | (data[Coe.bp3_0.value])
        otp = self.__convert_signed(otp, 15)
        self.k['bp3'] = self.__calc_k('bp3', otp)
        
        # 温度計測が無効化されている場合に備えて25℃としておく
        self.k['tr'] = 25.0 * 256.0

    def __set_powermode(self, mode):
        """
        電源モードを設定する．
        
        Parameters
        ----------
        mode : int
            電源モードの指定．
        """
        if SMBUS:
            data = self.bus.read_i2c_block_data(self.config['address'], REG_CTRL_MEAS, CTRL_MEAS_LENGTH)
            len = CTRL_MEAS_LENGTH
        else:
            len, data = self.pi.i2c_read_i2c_block_data(self.qmp6988, REG_CTRL_MEAS, CTRL_MEAS_LENGTH)
        if (len == CTRL_MEAS_LENGTH):
            value = data[0] & 0xFC
            
            value |= mode & 0x03
            if SMBUS:
                data = self.bus.write_i2c_block_data(self.config['address'], REG_CTRL_MEAS, [value])
            else:
                self.pi.i2c_write_i2c_block_data(self.qmp6988, REG_CTRL_MEAS, [value])
            time.sleep(0.02)

    def __set_oversampling(self, mode, sampling):
        """
        センサのオーバーサンプリングを設定する．
        
        Parameters
        ----------
        mode : string
            センサの指定．
        sampling : int
            オーバーサンプリングの設定値．
        """
        if (mode == 'temperature'):
            offset = 5
            mask   = 0x1F
        elif (mode == 'pressure'):
            offset = 2
            mask   = 0xE3
        else:
            return
        
        if SMBUS:
            data = self.bus.read_i2c_block_data(self.config['address'], REG_CTRL_MEAS, CTRL_MEAS_LENGTH)
            len = CTRL_MEAS_LENGTH
        else:
            len, data = self.pi.i2c_read_i2c_block_data(self.qmp6988, REG_CTRL_MEAS, CTRL_MEAS_LENGTH)
        if (len == CTRL_MEAS_LENGTH):
            value = data[0] & mask
            
            value |= (sampling & 0x07) << offset
            if SMBUS:
                data = self.bus.write_i2c_block_data(self.config['address'], REG_CTRL_MEAS, [value])
            else:
                self.pi.i2c_write_i2c_block_data(self.qmp6988, REG_CTRL_MEAS, [value])
            time.sleep(0.02)

    def __set_filter(self, filter):
        """
        IIR filterを設定する．
        
        Parameters
        ----------
        filter : int
            IIR filterの設定値．
        """
        value = filter & 0x07
        if SMBUS:
            data = self.bus.write_i2c_block_data(self.config['address'], REG_IIR_CNT, [value])
        else:
            self.pi.i2c_write_i2c_block_data(self.qmp6988, REG_IIR_CNT, [value])
        time.sleep(0.02)

    def __convert_signed(self, value, signed_bit):
        """
        符号bitに合わせてunsigned intからintへ変換する．

        Parameters
        ----------
        value : int
            変換対象の値．
        signed_bit : int
            符号bitの桁．

        Returns
        -------
        result : int
            変換した値．
        """
        if (value >= (1 << signed_bit)):
            value -= (1 << (signed_bit + 1))
        
        return value
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

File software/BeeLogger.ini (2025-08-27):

## General section
[General]

# USB drive name
# Comment out to log on SD
driveName = BEELOGGER

# Flag to set timed logging
logStop = False

# rPi restart flag
rstEn = True

# Illumination turn on and off times 5:00 - 20:30
lightOn_hour = 5
lightOn_minute = 00

lightOff_hour = 20
lightOff_minute = 30

# Logging stop time
logOff_year = 2022
logOff_month = 4
logOff_day = 8
logOff_hour = 10
logOff_minute = 00


## Sensor thread cfg
[Sensors]
# Sensor ports

# Sensor read period [s] 900
period_threadSensors = 60

# Record time - mic [s] 30
recordTime = 10

## Camera thread cfg
[Camera]
# Capture settings ({exp} = 1us)
fps = 5
exp = 1000
iso = 400

# ROI (set all parameters as image coordinates)
left = 0
top = 240
right = 1280
bottom = 480

# Image logging decimation factor
log_dec = 1

[LightingPWM]
freq_PWM   = 1000

#port_PWM_0 = White
port_PWM_0 = 18
duty_PWM_0 = 0

#port_PWM_1 = Green
port_PWM_1 = 13 
duty_PWM_1 = 0

#port_PWM_2 = IR 
port_PWM_2 = 16
duty_PWM_2 = 100

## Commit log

2022-03-03 Added ini file, sensors rewriten to objects
2022-03-03 Cleanup #1
    New directory structure, draft of the camera class
2022-03-16 Implementation of microphone, sensor thread ready for testing
2022-03-24 First implementation of camera, functional microphone
2022-03-31 Release 1.0
    New organisation, threads are called periodically from main.
2022-06-01 SGP30 update
    SGP30 sensor works in separate thread now in order to allow dynamic calibration.
2022-06-22 added mechanic parts
    [bottom.STL, glass_light_chamber.DXF, main_frame.STL, middle.STL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]
2022-07-11 QMP implementation
    Implementation of the QMP pressure sensor
2022-07-14 added hardware readme
    [battery_pack.STL]
2022-07-20 BeeCounter bug fix
    Fixed the bug with the BeeCounter thread - constructed and closed by Camera class now.
2022-09-16 added main glass dxf
    [glass.DXF]
2023-03-19 Libraries and code for Raspberry Pico
2025-08-18 Sensor refactoring
    Refactoring of sensors, removal of the Grove library. Camera is not implemented yet.
    [SensorLog.csv]
2025-08-19 Removing the log
    [SensorLog.csv]
